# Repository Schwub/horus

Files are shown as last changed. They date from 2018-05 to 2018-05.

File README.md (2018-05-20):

# Horus

# Work in Progress !!
# English version comming soon !!

## Einleitung
Dies ist ein Projekt des

[Department of Conservative Dentistry and Periodontology](http://www.klinikum.uni-muenchen.de/Poliklinik-fuer-Zahnerhaltung-und-Parodontologie/de/index.html),
University Hospital, LMU Munich, Germany

unter der Leitung von [Herrn Prof. Dr. Karl-Heinz Kunzelmann](http://www.dent.med.uni-muenchen.de/~kkunzelm/htdocs/index.html).

Das Projekt basiert auf der eindrucksvollen Arbeit von [Jesús Arroyo Torrens](https://github.com/Jesus89) im Zusammenhang mit dem [Cyclop 3D-Scanner](https://github.com/LibreScanner/ciclop).

Unser Projekt hatte mehrere Teilziele:

- Unterstützung von Industriekameras der Firma IDS
- Softwareunterstützung einer linearen Bewegung des Probentisches als Ergänzung zur Rotation des Probentisches des Original Cyclop Scanners
- Entwicklung eines einfachen 3D-Scanners mit linearer Bewegung des Probentisches unter Verwendung der Horus Firmware

Obwohl zahlreiche 3D Scanner auf Grundlage von Lasertriangulation kommerziell angeboten werden, war es schwer, einen Scanner zu finden, der alle unsere Anforderungen erfüllen konnte:

- Open Source Software
- Kostengünstige Hardware, die flexibel an unterschiedliche Meßanforderungen angepaßt werden kann
- Hohe Auflösung, z.B. 20 µm zur Vermessung von Zähnen
- Vermessung von Objekten unterschiedlicher Größe
- einfache Kalibrierung

Kostengünstige, kommerziell verfügbare Scanner sind meist für unsere Zwecke nicht genau genug, während Spezialscanner, beispielsweise für die Anwendung in der zahnmedizinischen Forschung, entweder keine geeigneten Schnittstellen für die Daten anbieten, die Daten durch Glätten und Komprimieren nicht die gewünschte Detailqualität bieten oder einfach unangemessen teuer sind.

Der [Ciclop 3D-Scanner](https://github.com/LibreScanner/ciclop) stellt einen sehr kostengünstigen Einstieg in die 3D Scan Techanik dar. Sie können sich anhand der [deutschen Einführung](http://diwo.bq.com/de/einfuhrung-ciclop-und-horus/) oder [englischen Einführung](http://diwo.bq.com/en/presentation-ciclop-horus/) rasch einen Überblick über das BQ Ciclop Projekt verschaffen. Besonders hervorheben möchten wir, dass sowohl der [theoretische Hintergrund des Scanners](https://github.com/Jesus89/3DScanScience) als auch die Software [Horus](http://horus.readthedocs.io/en/release-0.2/) zur Steuerung des Scanners hervorragend dokumentiert sind. Die Software hat außerdem die nötige Flexibilität für eigene Weiterentwicklungen mit akzeptablem Aufwand.

Unsere Arbeitsgruppe beschäftigt sich seit fast 30 Jahren mit der Entwicklung und Anwendung von 3D Scannern in der Zahnmedizin ([A New Optical 3-D Device for the Detection of Wear, Journal of Dental Research 76(11):1799-807, 1997](DOI10.1177/00220345970760111201)). Während die Hardware dieser Scanner nach über 20 Jahren immer noch die erforderlichen Präzisionsmessungen erlaubt, ist die Lebenszeit der Computerhardware (Silicon Grafics, Irix Workstation) inzwischen abgelaufen, obwohl wir immer noch Messungen damit durchführen können. Das übergeordnete Ziel dieses Projektes ist es, die alte Hardware so zu modifizieren, dass sie in Zukunft in Kombination mit der Open Source Software von [Jesús Arroyo Torrens](https://github.com/Jesus89) verwendet werden kann. Langfristig streben wir an, auch andere Scanner, beispielsweise ältere 3Shape-Scanner, mit der neuen Software nachzurüsten (retrofitting).

Die Flexibilität der Scannersoftware von [Jesús Arroyo Torrens](https://github.com/Jesus89) erlaubt es jedoch, durch den Einsatz anderer Objektive, Kameras und Scannerrahmen, 3D-Scanner für fast alle Bedürfnisse mit sehr überschaubarem Aufwand zu realisieren.

In dieser Dokumentation wird ein einfacher Scanner beschrieben, auf dessen Grundlage wir die Software entwickelt und getestet haben. Das Prinzip dieses Scanners entspricht weitgehend dem mechanischen Aufbau unseres Dentalscanners ([A New Optical 3-D Device for the Detection of Wear, Journal of Dental Research 76(11):1799-807, 1997](DOI10.1177/00220345970760111201)). Der einfache Aufbau sollte nur als Träger für die Laser und Kameras dienen und war nie für Routinemessungen vorgesehen. Der Aufbau ist jedoch so zuverlässig und stabil, dass wir diesen einfachen 3D-Scanner inzwischen auch für wissenschaftliche Vermessungen verwenden. Der abgebildete Aufbau kostet je nach Qualität der verwendeten Komponenten ca. 1000 - 1400 €. Die hier genannten Komponenten können einfach bestellt werden. Für den Aufbau sind nur wenig Werkzeuge erforderlich. Einzelne Teile wurden mit einem 3D Drucker hergestellt. Nicht dargestellt ist ein 2-Achsen-Drehtisch für die Probenaufnahme, da die Software für dessen Steuerung noch nicht vollständig implementiert wurde. Als Steuerelektronik wurde ein Arduino Uno Microcontroller sowie ein ZUM Shield Clone (www.roboter-bausatz.de) verwendet. Das entspricht der Elektronik, die mit dem BQ Ciclop 3D-Scanner ausgeliefert wird. Als Firmware wird die [Horus Firmware](https://github.com/bqlabs/horus-fw) verwendet.

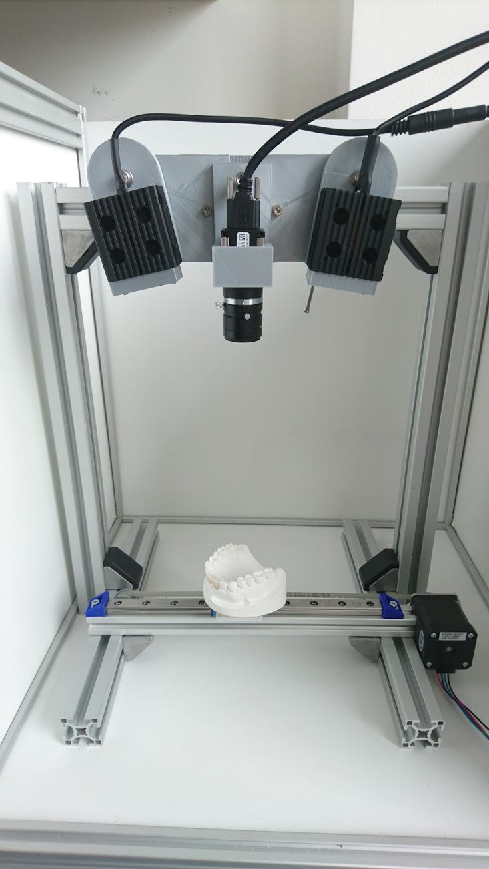
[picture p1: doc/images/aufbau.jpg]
Erweiterter Cyclop Scanner


Dieses Beispiel zeigt einen der ersten Scans eines Zahnes:
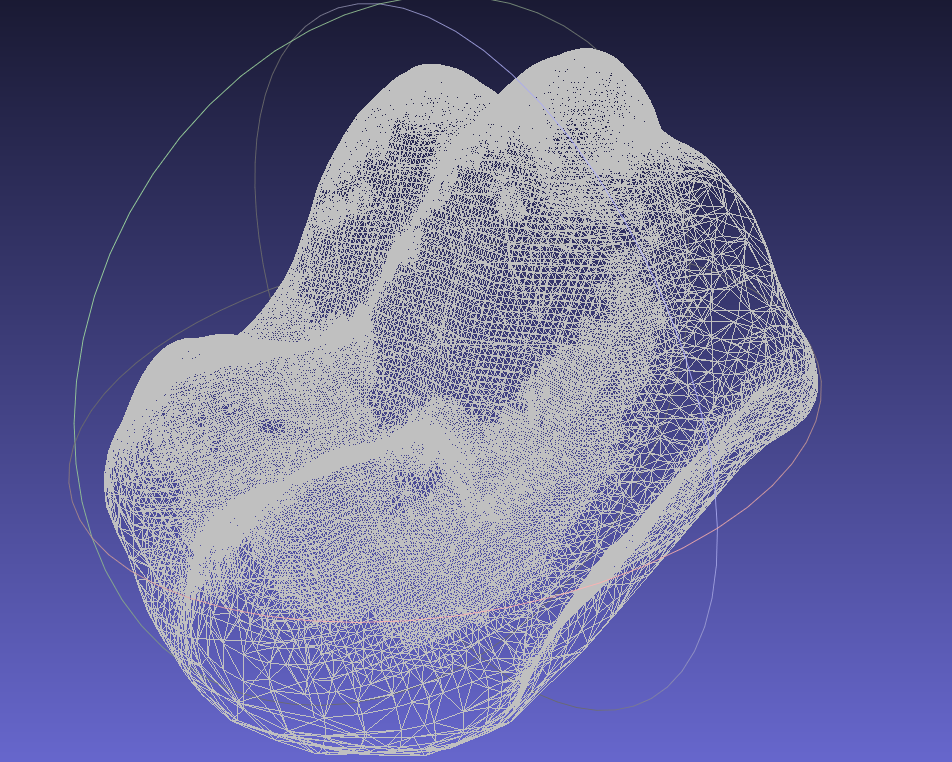
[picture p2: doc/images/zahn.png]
Beispiel Scan eines Zahnes


## Hardware

### Kamera
Anstelle der ursprünglich verwendeten Webcam Logitech C270 wurde eine Kamera mit C-Mount-Adapter verwendet. Durch den C-Mount-Adapter ist es möglich, Objektive mit unterschiedlicher Brennweite, manuellem Fokus und manueller Blendeneinstellung zu verwenden, was es wiederum erlaubt, den Messbereich individuell an die jeweiligen Bedürfnisse anzupassen. Die Wahl für die Kamera fiel auf ein Produkt der Firma [IDS](https://en.ids-imaging.com/home.html).

Für die Entscheidung, ein IDS Produkt zu wählen, war ausschlaggebend:

- Kompatibel mit Windows und GNU/Linux Betriebssystemen
- Industriequalität mit professionellem Langzeitsupport

Das konkret gewählte Kameramodell [UI-3160CP Rev. 2.1](https://en.ids-imaging.com/store/ui-3160cp-rev-2-1.html) hat u.a. folgende Eigenschaften

- USB 3.0 Schnittstelle
- Eine Auflösung von 1920x1200 Pixeln
- Bis zu 165 Bilder pro Sekunde bei voller Auflösung

Im Prinzip sollte man jedoch jede IDS Kamera verwenden können, die von der IDS Software Suite unterstützt wird.

#### Objektiv

Als Objektiv dient ein Tamron Objektiv (f/1.6-16, Focal Length 25mm, C-type lens mount, Type: AE.0051.2.10400.00, IDS).

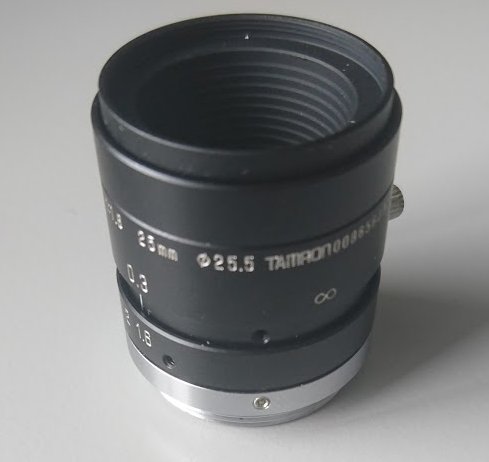
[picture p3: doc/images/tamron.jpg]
Tamron Objektiv


### Scankopf

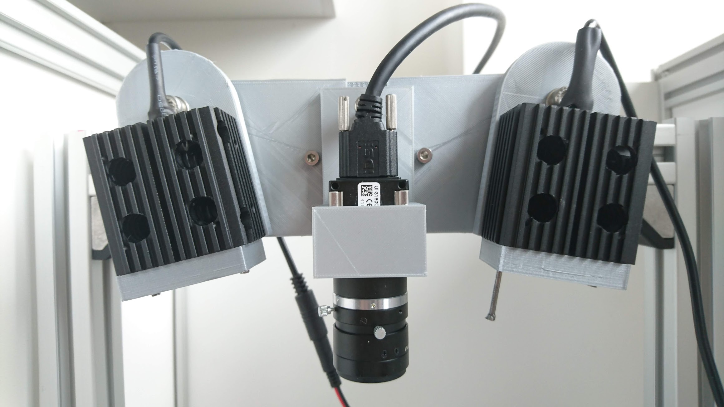
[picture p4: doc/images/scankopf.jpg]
Scankopf


Die Halterung des Scankopfes wurde mit einem 3D-Drucker erstellt. Die CAD-Files (Solidworks 2018) und STL Files befinden sich in dem Ordner [files](/files).

Der Scankopf besteht aus einer Halterung für die IDS Kamera und zwei Haltern für die Laserdioden, die in einen passenden Kühlkörper montiert sind. Die Lasersdiodenhalter lassen drehen, so dass die Laserlinie auf auf das Objekt justiert werden kann.

Für die Erzeugung der Laserlinien  wurde je ein Lasermodel CW532-001L (Roithner Lasertechnik) mit Zylinderlinse verwendet. Die Lasermodule wurden mit einem Kühlkörper SQ50 (Roithner Lasertechnik) am Scankopf befestigt. Die von dem Lasermodul erzeugte Laserlinie war für unsere Makrovermessungen zu breit und wurde deshalb mit einer achromatischen Sammellinse zusätzlich fokussiert. Der Abstand zwischen den beiden Laserdioden und der Kamera ist aktuell fest vorgegeben, der Winkel der Laserlinien kann im Rahmen der Schärfentiefe des Kameraobjektivs und der achromatischen Sammellinse frei eingestellt werden (was Einfluss auf den Triangulationswinkel hat).

TODO: Laser einstellen.

### Scantisch

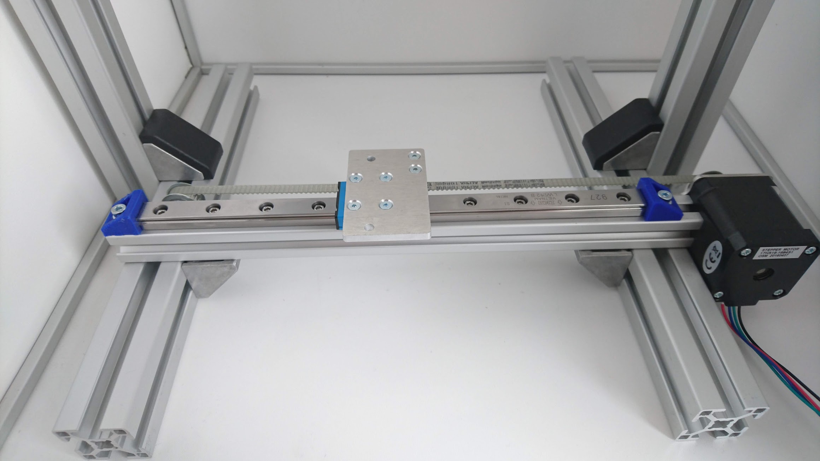
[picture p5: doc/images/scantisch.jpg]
Scantisch


Der Scantisch besteht aus einer einfachen Linearführung mit Profilschiene, die über einen Zahnriemen von einem NEMA 17 Schrittmotor positioniert wird. Auf dem Wagen der Linearführung können unterschiedliche Probenhalter montiert werden, aktuell ist auf den Bildern eine Alu-Platte als Probentisch zu sehen, die mit der Linearführung mitgeliefert worden war.

### Kalibriertisch

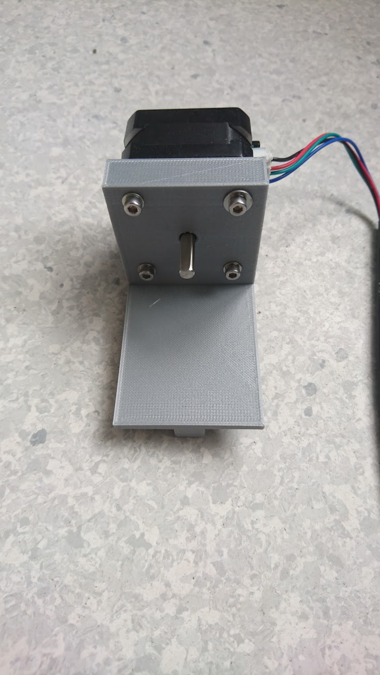
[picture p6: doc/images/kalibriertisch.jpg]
Kalibriertisch


Der Kalibriertisch wird benötigt um die Parameter des Scanner zu setzten.
Der Kalibriertisch wird mittig auf dem Scantisch angebracht.
Das Schachbrettmuster wird während dem Kalibrierungsprozesses um die eigenen Achse gedreht, während die Laser
jeweils eine Linie projizieren. Durch die Rotation erkennt der Scanner die Tiefenverhältnisse des Scanbereichs.

### Materialliste

[Bill of materials (BOM)](/files/BOM-Laserscanner.ods)

Anzahl|Beschreibung|Artikelnummer|Bezugsquelle|Kosten in Euro (circa), Stand: 2017
------------ | -------------| -------------| -------------| -------------
2|Linse zur Fokussierung der Laserdiode, Achromat, D=25.4mm, F=300mm|AC254-300-A|Thorlabs|90 €
1|Kamera IDS, UI-3160CP-M-GL Rev.2|AB00687|IDS|720 €
1|USB3 Standardkabel 3m|AD00142|IDS|30 €
1|Objektiv, Tamron, M118FM25, 25 mm, C-Mount, Manuell Fokus/Iris mit Lock, 2 Megapixel|AE.0051.2.10400.00|IDS|180 €
2|GREEN DPSS LASER MODULES|CW532-001L |Roitner Lasertechnik|48 €
2|Heat Sink|SQ50 |Roitner Lasertechnik|22 €
2|Laser Power Supply 3V|LPS31 |Roitner Lasertechnik|24 €
1|Lineareinheit M200 mit 210 mm Hub|931-0011|Multec GmbH|200 €
5|Aluprofil 30x30 B-Typ Nut 8 Länge 290 mm|19617|Motedis GmbH|10 €
1|Hammermutter B-Typ Nut 8, Größe:M4, 1 Beutel (a 100 Stück)|096H08415|Motedis GmbH|13 €
1|Winkel 30 B-Typ Nut 8, mit Befestigungssatz und Abdeckkappe, 1 Beutel (a 10 Stück)|093W303N08|Motedis GmbH|16 €
1|NEMA17 12.7Ncm, Titan-Slimline Stepper Motor, D shaft |nema17-127n-titan |youprintin3d.de|16 €
1|ZUM Scan Shield für Ciclop 3D-Scanner| RBS11414 | anzado GmbH, Saarbrücken | 15 €
1|Arduino UNO Clone| ---  | ---  | 5 €

### Bezugsquellen

- Thorlabs GmbH, Hans-Böckler-Strasse 6, D-85221 Dachau, Germany
- IDS Imaging Development Systems GmbH, Dimbacher Str. 6-8, D-74182 Obersulm, Germany
- Roithner Lasertechnik GmbH, Wiedner Hauptstrasse 76, A-1040 Wien, Österreich
- Motedis GmbH, Stöckerweg 122, D-66806 Ensdorf, Germany
- Multec GmbH, Hauptstr. 11, 88377 Riedhausen, Germany
- You-Print-In-3D, Evgenia Deinzer, Stephanienstr. 55, 76133 Karlsruhe, Germany
- anzado GmbH, Römerstadt 2-4, 66121 Saarbrücken, Germany

### Aufbau

#### Scankopf
TODO

#### Scankopf drucken
TODO

#### Kamera montieren
TODO

#### Linsen anbringen
TODO

#### Halterung montieren
TODO

#### Laser anbringen
TODO

### Scantisch
TODO

### Rahmen
TODO

## Änderungen der Software

### Kamera-Treiber
Um die IDS Ueye Kamera in der Python Software Horus nutzen zu können, wurden für dieses Projekt eigene Wrapper mit Cython geschrieben. Die Funktionalität der von IDS angebotenen C Funktionen wurden abstrahiert und vereinfacht.

Cython ist eine Python ähnliche Programmiersprache, die nach C kompiliert wird. Da die Standard Python Implementierung ebenfalls in C geschrieben ist, können C-Module in Python aufgerufen werden.

Der Wrapper kann in folgendem Github-Repository gefunden werden [Cyueye](https://github.com/Schwub/cyueye). Genaue Information zu den vorgenommenen Code-Änderungen finden sie in der Datei */doc/development/cyueye.md* in diesem Repository.

### Punktewolke generierung
TODO

### Scantisch Steuerung
TODO

### Installation der Software
TODO

## Scanprozess
TODO

# Acknowledgement

Wir möchten uns bei Hr. Martin Lotz bedanken, der die Konstruktionszeichnungen erstellt hat.

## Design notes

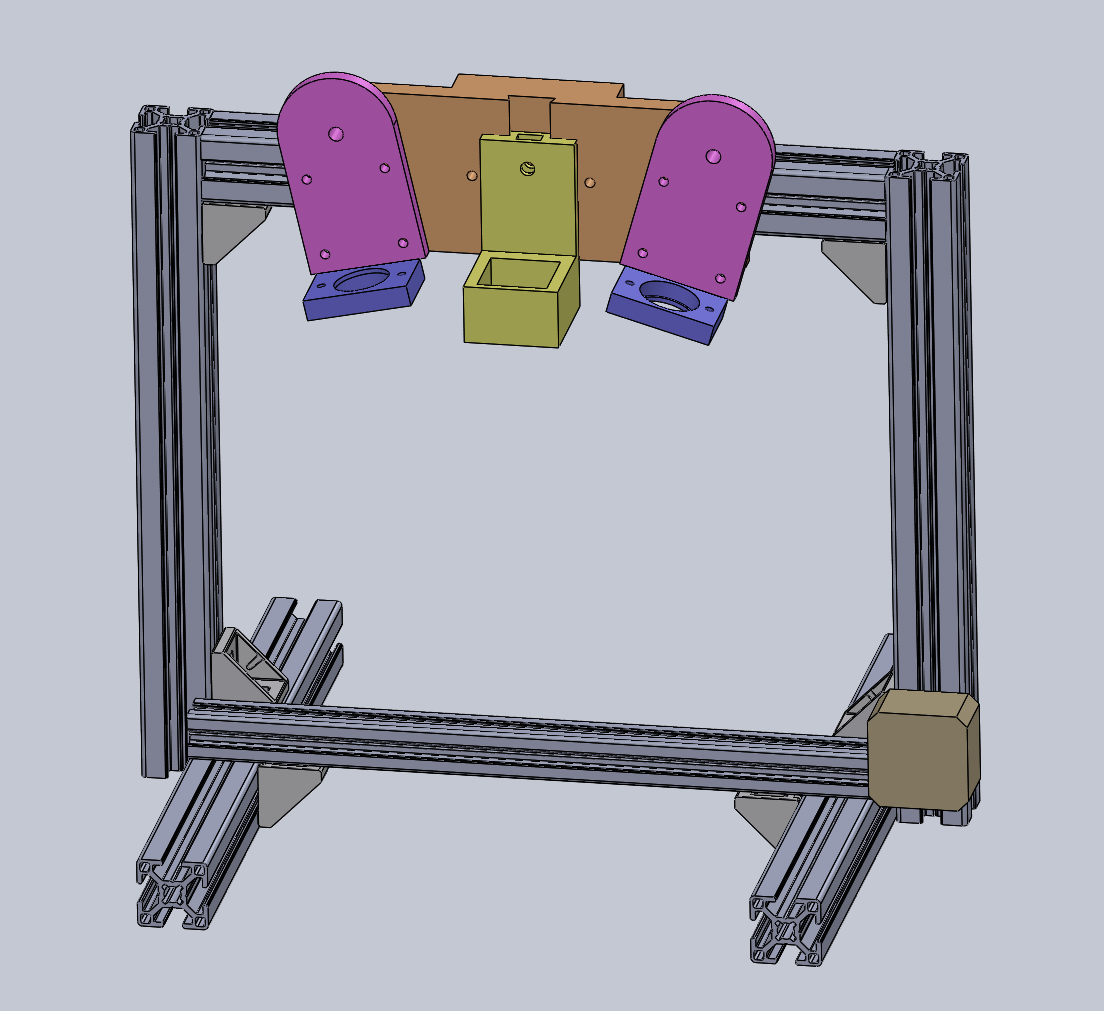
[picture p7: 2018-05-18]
doc/images/cad-scanner.PNG

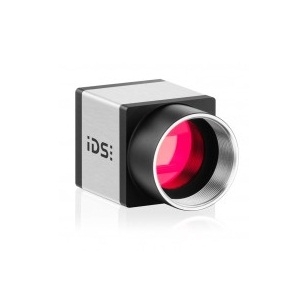
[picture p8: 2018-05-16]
doc/images/kamera.jpg

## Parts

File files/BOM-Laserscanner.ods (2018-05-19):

BOM Laserscanner
Anzahl | Beschreibung | Artikelnummer | Bezugsquelle | Kosten in Euro (circa), Stand: 2017
2 | Linse zur Fokussierung der Laserdiode, Achromat, D=25.4mm,F=300mm | AC254-300-A | Thorlabs | 90,00 €
1 | Kamera IDS, UI-3160CP-M-GL Rev.2 | AB00687 | IDS | 720,00 €
1 | USB3 Standardkabel 3m | AD00142 | IDS | 30,00 €
1 | Objektiv, Tamron, M118FM25, 25 mm, C-Mount, Manuell Fokus/Iris mit Lock, 2 Megapixel | AE.0051.2.10400.00 | IDS | 180,00 €
2 | GREEN DPSS LASER MODULES | CW532-001L | Roitner Lasertechnik | 48,00 €
2 | Heat Sink | SQ50 | Roitner Lasertechnik | 22,00 €
2 | Laser Power Supply 3V | LPS31 | Roitner Lasertechnik | 24,00 €
1 | Lineareinheit M200 mit 210 mm Hub | 931-0011 | Multec GmbH | 200,00 €
5 | Aluprofil 30x30 B-Typ Nut 8 Länge 290 mm | 19617 | Motedis GmbH | 10,00 €
1 | Hammermutter B-Typ Nut 8, Größe:M4, 1 Beutel (a 100 Stück) | 096H08415 | Motedis GmbH | 13,00 €
1 | Winkel 30 B-Typ Nut 8, mit Befestigungssatz und Abdeckkappe, 1 Beutel (a 10 Stück) | 093W303N08 | Motedis GmbH | 16,00 €
1 | NEMA17 12.7Ncm, Titan-Slimline Stepper Motor, D shaft | nema17-127n-titan | youprintin3d.de | 16,00 €
1 | ZUM Scan Shield für Ciclop 3D-Scanner | RBS11414 | www.roboter-bausatz.de, anzado GmbH, Saarbrücken | 15,00 €
1 | Arduino UNO Clone | --- | --- | 5,00 €

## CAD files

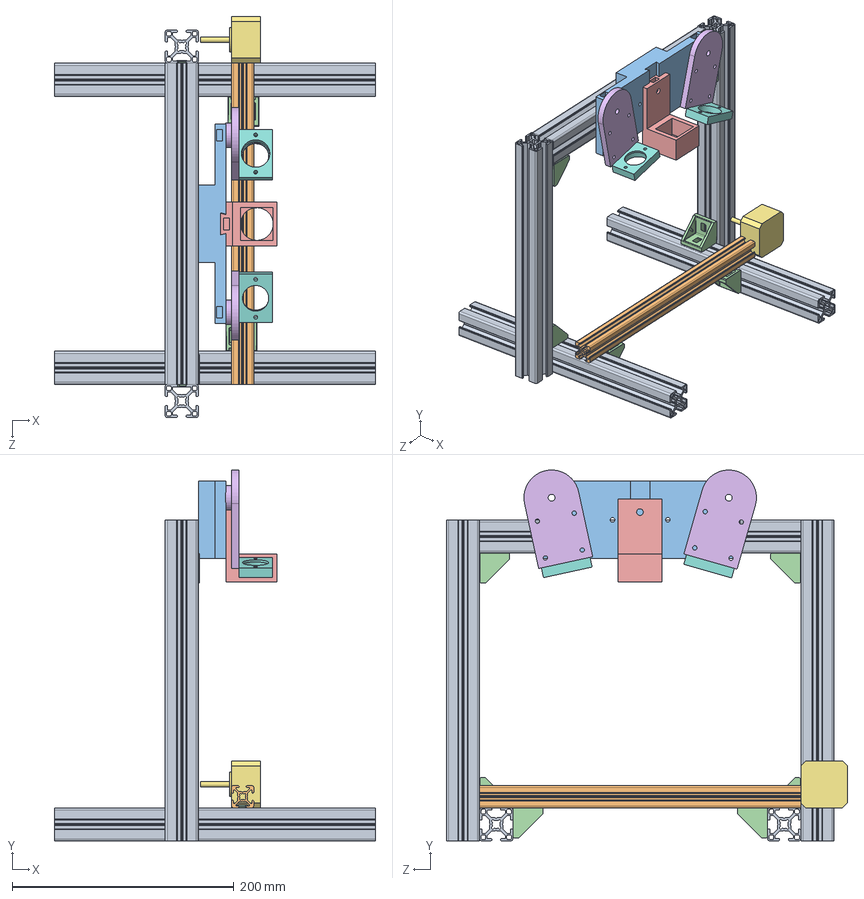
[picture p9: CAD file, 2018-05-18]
files/solidworks/Assembly.SLDASM
290.0 x 335.0 x 362.3 mm
290_Aluprofil_30x30 x 5
290_Aluprofil_20x20
Kamerahalterung_Profil
Bracket_30_B-Type_slot_8 x 6
Kamerajustierungshalterung_IDS_linear
Laserhalterung x 2
Nema_17_slim
Linsenhalter x 2

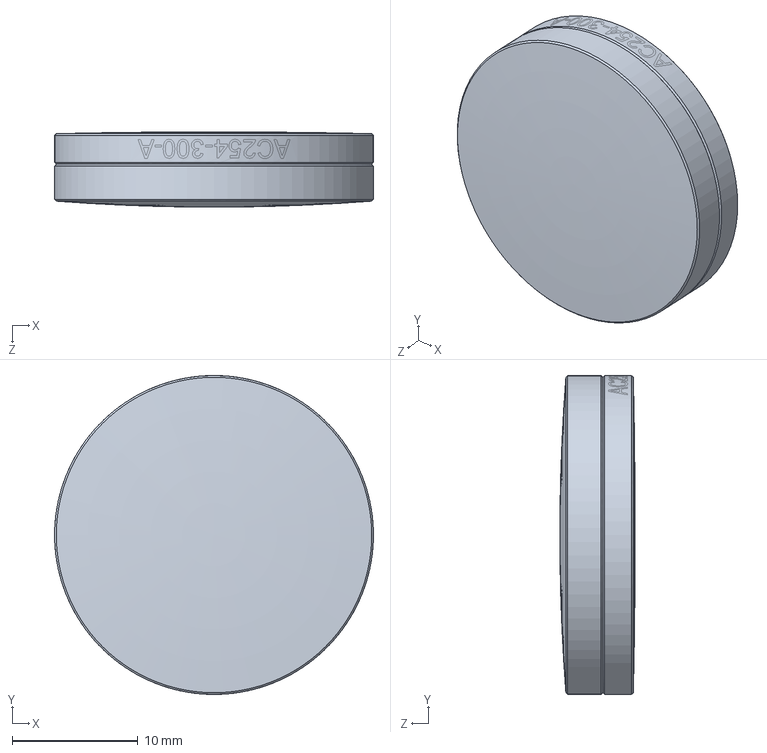
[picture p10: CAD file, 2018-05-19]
files/solidworks/Achromat-Sammellinse-AC254-300-A-Solidworks.sldprt
25.4 x 25.4 x 6.00 mm

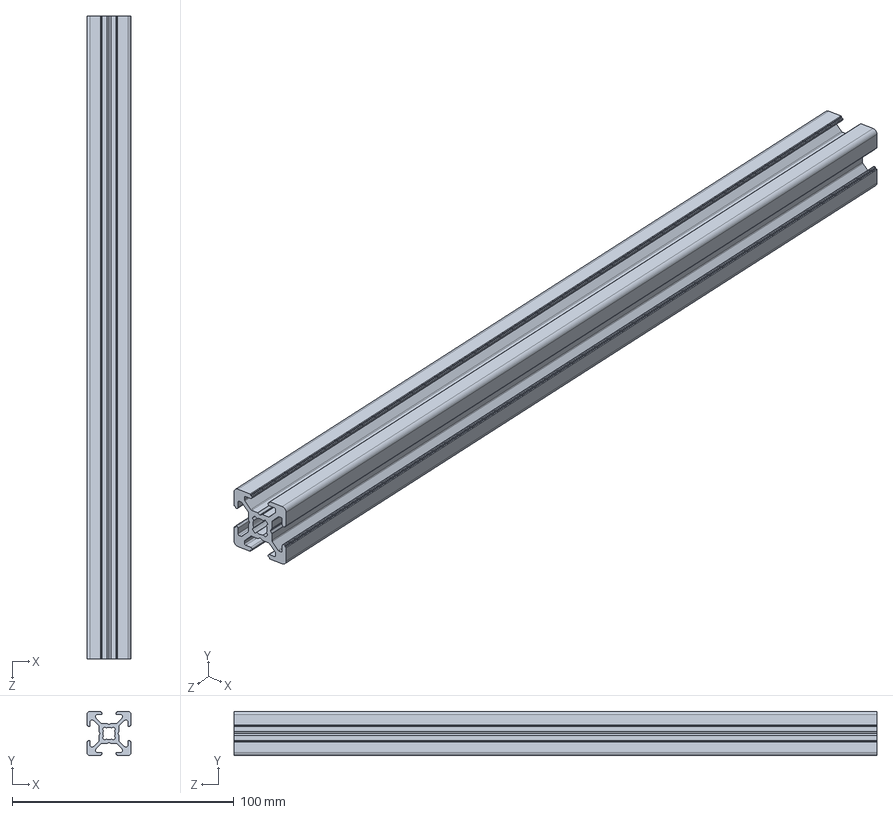
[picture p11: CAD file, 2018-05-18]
files/solidworks/290_Aluprofil_20x20.SLDPRT
20.0 x 20.0 x 290.0 mm

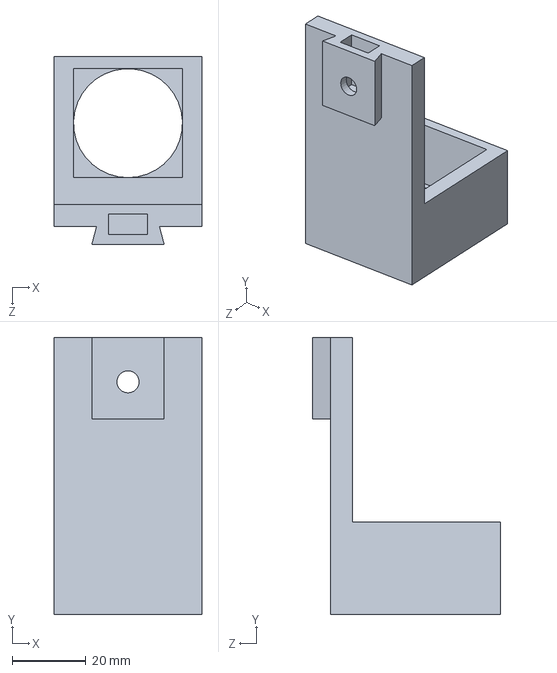
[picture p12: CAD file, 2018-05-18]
files/solidworks/Kamerajustierungshalterung_IDS_linear.SLDPRT
40.0 x 75.0 x 50.8 mm

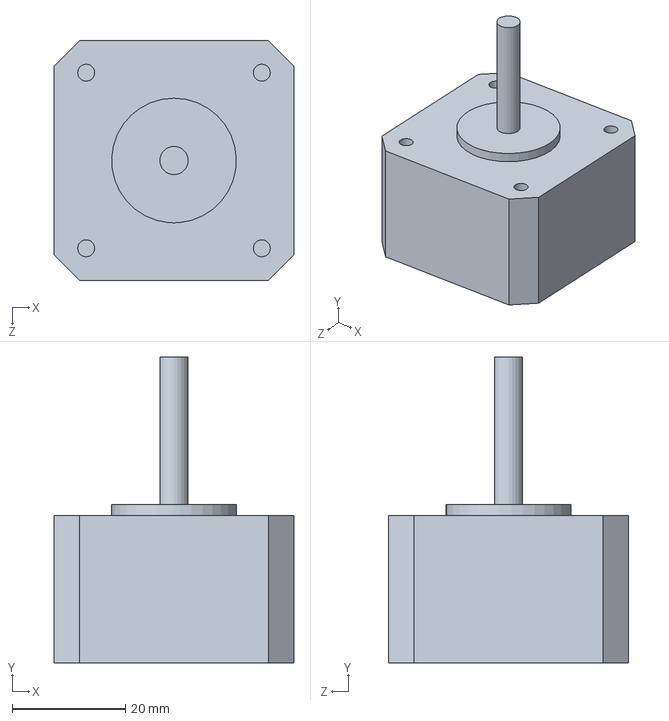
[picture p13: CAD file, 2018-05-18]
files/solidworks/Nema_17_slim.SLDPRT
42.3 x 54.0 x 42.3 mm

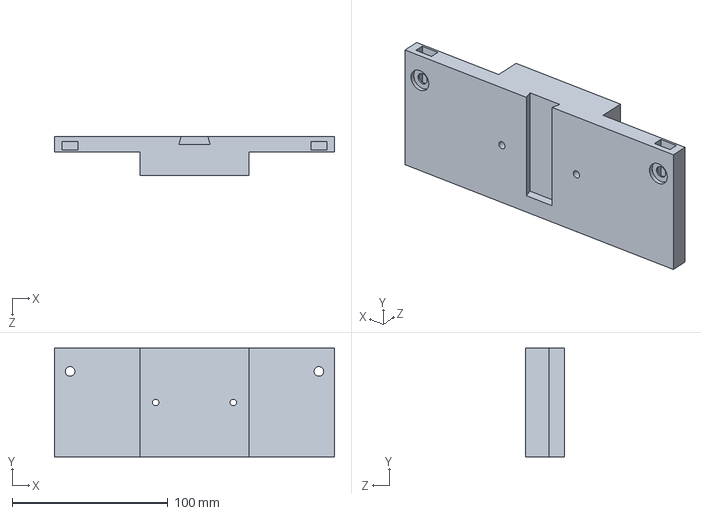
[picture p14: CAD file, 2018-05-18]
files/solidworks/Kamerahalterung_Profil.SLDPRT
180.0 x 70.0 x 25.0 mm

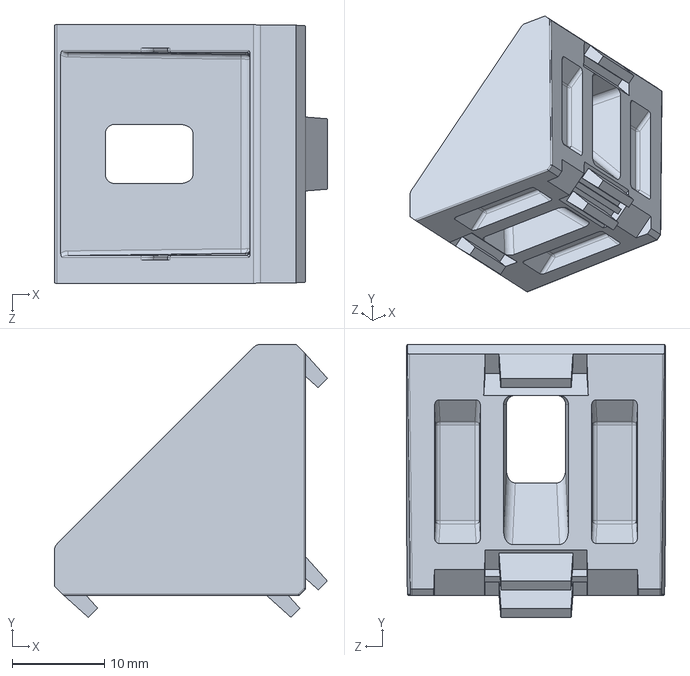
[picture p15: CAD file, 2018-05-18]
files/solidworks/Bracket_30_B-Type_slot_8.SLDPRT
29.6 x 29.6 x 28.0 mm

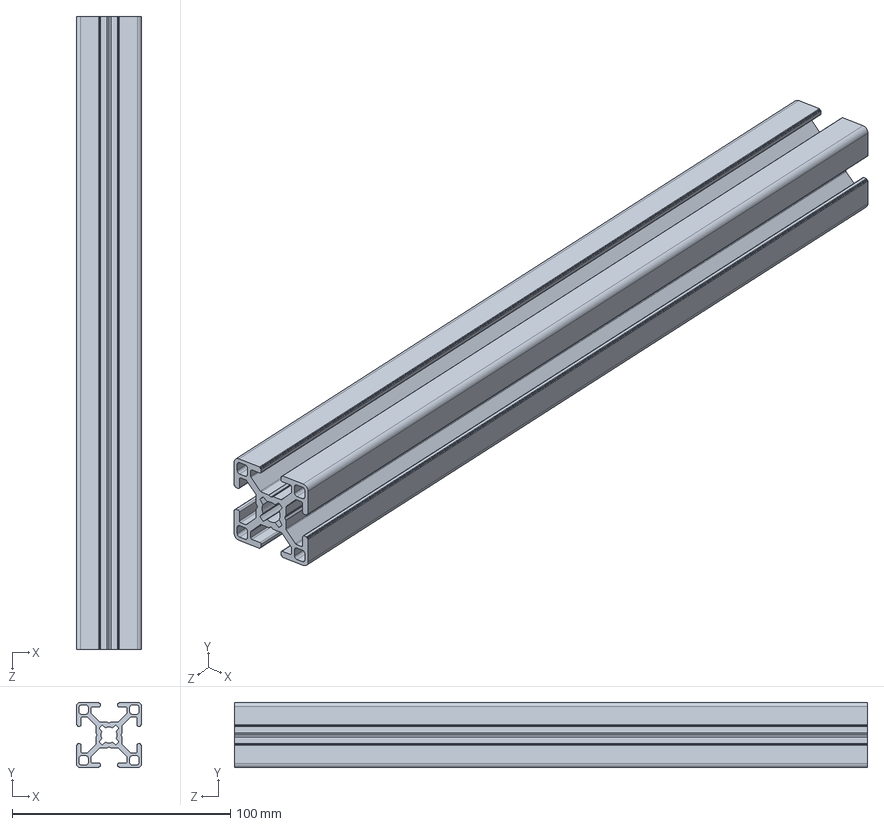
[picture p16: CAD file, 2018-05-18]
files/solidworks/290_Aluprofil_30x30.SLDPRT
30.0 x 30.0 x 290.0 mm

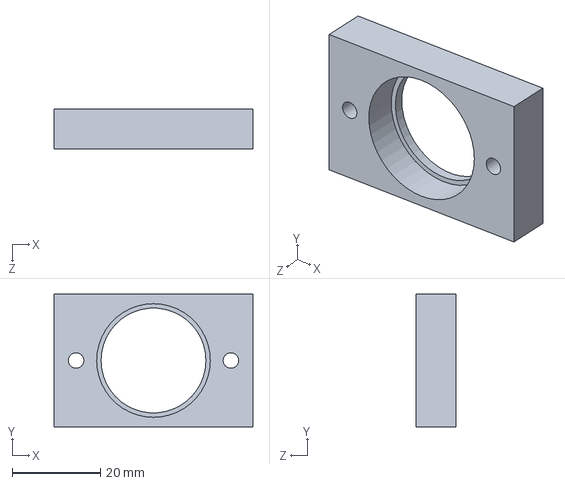
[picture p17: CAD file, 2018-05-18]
files/solidworks/Linsenhalter.SLDPRT
45.0 x 30.0 x 9.00 mm

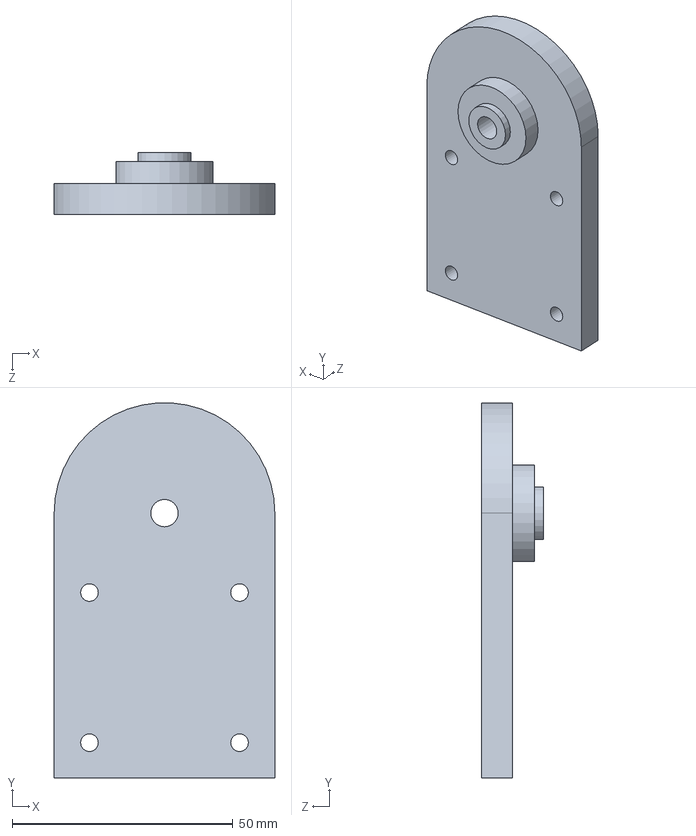
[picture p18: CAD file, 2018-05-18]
files/solidworks/Laserhalterung.SLDPRT
50.0 x 84.9 x 14.0 mm

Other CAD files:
files/stl/Kamerahalterung_Profil.STL
files/stl/Kamerajustierungshalterung_IDS_linear.STL
files/stl/Laserhalterung.STL
files/stl/Linsenhalter.STL

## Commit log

2018-05-18 added CAD files
    [290_Aluprofil_20x20.SLDPRT, 290_Aluprofil_30x30.SLDPRT, Assembly.SLDASM, Bracket_30_B-Type_slot_8.SLDPRT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]
2018-05-18 added BOM
    [BOM-Laserscanner.ods]
2018-05-18 added stl files
    [Kamerahalterung_Profil.STL, Kamerajustierungshalterung_IDS_linear.STL, Laserhalterung.STL, Linsenhalter.STL]
2018-05-19 added further details in the documentation
    [BOM-Laserscanner.ods]
